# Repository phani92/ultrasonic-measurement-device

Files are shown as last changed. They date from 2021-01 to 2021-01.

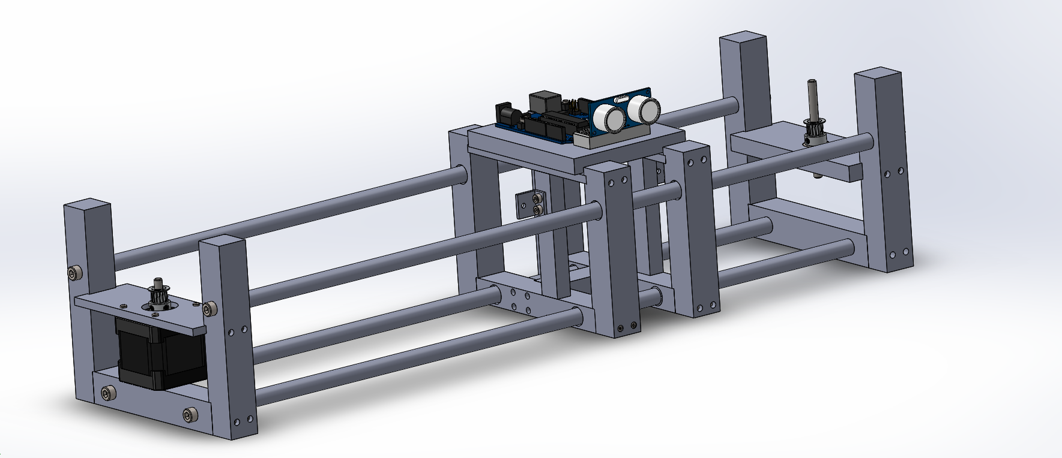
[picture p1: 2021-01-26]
cad files/assembly-bild.PNG

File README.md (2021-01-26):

# ultrasonic-measurement-device
A measurement setup using ultrasonic sensor and single axis linear system

Introduction:

Our aim for the scientific project was to develop a measurement setup that emits and receives ultrasound. The received data should be processed to a 1D ultrasound image. In addition, the influence of the control of the ultrasonic transmitter on the measured data is to be investigated.

Hence first we started with the basics of ultrasonic sensor its working principle and then we implemented the basic application of ultrasonic sensor for sensing distance with the help of Arduino and serial monitor. We displayed the distance real time in the serial monitor.

As per the problem statement, we need to now develop a measurement setup which can map sensor data. For this, we finalized on a linear guide system with Arduino as a slave and MATLAB as the main controller.

Ultrasonic Sensor:

Ultrasonic sensors emit short, high-frequency sound pulses at regular intervals. These propagate in the air at the velocity of sound. If they strike an object, then they are reflected as echo signals to the sensor, which itself computes the distance to the target based on the time- span between emitting the signal and receiving the echo.

As the distance to an object is determined by measuring the time of flight and not by the  intensity  of  the  sound,  ultrasonic  sensors  are  excellent  at  suppressing  background interference. Virtually all materials which reflect sound can be detected, regardless of their colour. Even transparent materials or thin foils represent no problem for an ultrasonic sensor. Ultrasonic sensors can see through dust-laden air and ink mists.

Even thin deposits on the sensor membrane do not impair its function. Sensors with a blind zone of only 20  mm and an extremely thin beam  spread are making entirely new applications possible today: Fill level measurement in wells of microtiter plates and test tubes, as well as the detection of small bottles in the packaging industry, can be implemented with ease. Even thin wires are reliably detected.



Mechanical Experimental Setup:

We selected a linear axis movement system so that the system can move automatically without any human errors or disturbance and the sensor can be studied more precisely and accurately. The idea of this system is to move it linearly in a single direction over a distance and to study the objects placed in its vicinity. The objects distance from this system and width of the object can be recorded with the help of ultrasonic sensor placed on the movable body.

Another advantage of this design is that we can study other sensors also by replacing the sensor and the respective program in Matlab. This design also gives a liberty to extend the observable area or study area by unbolting the ends and extending the linear guides.

In the initial phase of the project we have designed a single axis linear motion guide with the idea of using lead screw as shown below. The detachable holder with the ultrasonic sensor and Arduino setup can be placed over the moving unit in the above shown setup.



To have smooth movement such that the vibrations can be minimised and does not affect the study of sensor, the lead screw system was replaced with a pulley and belt system.

In the below figure, it can be noticed that the centre body is elevated to 5mm with respect to the corner holding stands. This is to allow the centre body to move freely. The idea of this setup is to pull the centre body from one end to another end with the help of a belt and a pulley system. Belt is hinged to the centre body.



The setup consists of three main mechanical parts.

1. Vertical Holding stands and linear guides

These stands are on both the corners of the setup and are heavy to give enough strength to the system such that the vibrations are absorbed, and the entire system stays stable on a surface. These stands are further drilled on 4 places so that the linear guides can be inserted into them and be bolted on the outer corners. There is also a flat plate on both the ends to mount the pulley and motor.

The pulley is mounted and free to rotate with the help of a ball bearing. The dimensions of these stands and bearings are provided in the design files that are attached in the appendix.



2. Centre Holding body

The centre body is to facilitate free movement for the sensor. This body lies on top of 4 linear guides. It has linear bearings to provide frictionless movement and is connected to the belt on both the ends which provide a pull force allowing for a movement in both the directions. The sensor along with Arduino and bread board for ultrasonic sensor are mounted on top of this setup. The entire metal frame holding the sensor and Arduino setup can be detached from the centre body by unbolting. It is feasible to use the sensor setup alone without the entire system. Just by unbolting two screws the sensor setup can be unmounted from the body.



3. Belt and pulley system

The belt is connected to both the ends of the centre of the body and the belt passes through the pulley and motor shaft thereby forming a closed-circuit system.  By pulling one of the ends of the body, it enables the body to travel in that direction. Nema 17 Stepper motor is used as it can provide a torque of 1.6 Kg / cm. The centre body weight around 700 grams and the torque provided by the motor is enough to move the body linearly.



The system was designed in SolidWorks and realised in workshop. All the files for individual tiles and the detail list of parts are shared in appendix. 

Solid Works Design:



Realised Setup:

Top View



Side View



Electronic Components:

We have used MATLAB platform to run our setup. Hence the Arduino Uno is used as a passive board. The electrical setup is as shown below.



The Electronic components used are: Ultrasonic sensor:

Here, we are using the HC-SR04 ultrasonic sensor. The big advantage of this sensor its available easily and very cheap compared to other ultrasonic sensors.



Specifications:

|Power Supply |+5V DC |
| - | - |
|Quiescent Current |<2mA |
|Working Current |15mA |
|Effectual Angle |<15 Degree |
|Ranging Distance |2-400 cm |
|Resolution |0.3 cm |
|Measuring Angle |30 Degree |
|Trigger Input Pulse width |10 s |
|Dimension |45mm x 20mm x 15mm |
|Weight approx |10 g |
Ultrasonic sensor has a transmitter and a receiver in one module. The transmitter has a piezo which vibrates at a frequency of 45 kHz. The working principle of this module is as shown in figure 1. The ultrasonic sensor is trigger by making Trigger pin high for 10us. Then 8 pulses of 40kHz is send and the echo is received by the receiver part of sensor. 



As discussed earlier, Ultrasonic sensor is used to detect the distance of an object. This is done by time of flight concept. Here we have a proportional relationship between time and distance.

Arduino Uno:

We established a communication between Arduino Uno and MATLAB. We first need to install Hardware support packages for Arduino Uno, HC-SR04 sensor. Once the Hardware packages are installed we can establish MATLAB and Arduino communication. Please see the appendix for the MATLAB code.

Arduino Uno is a microcontroller board based on the ATmega328P. It has 14 digital input/output pins (of which 6 can be used as PWM outputs), 6 analogue inputs, a 16 MHz quartz crystal, a USB connection, a power jack, an ICSP header and a reset button. It contains everything needed to support the microcontroller; simply connect it to a computer with a USB cable or power it with an AC-to-DC adapter or battery to get started.



Specifications:

|Microcontroller |ATmega328P |
| - | - |
|Operating voltage |5V |
|Number of Analog input pins |6 |
|Flash memory |32KB |
|Clock speed |16Mhz |
|DC current for 3.3v pin |50 mA |

Adafruit Motor shield v2.3:

The Motor shield is used as a driver for stepper motor. The stepper motor needs 0.33A of current to run at 12V DC. The Motor shield provides a 1.2A peak current per phase. We can connect 2 stepper motors with this shield at the same time. We have connected our Stepper motor at M1 and M2 as it’s a bipolar stepper motor.



Specifications :

- 2 connections for 5V 'hobby' servos connected to the Arduino's high-resolution dedicated timer - no jitter!
- 4 H-Bridges: TB6612 chipset provides 1.2A per bridge (3A for brief 20ms peaks) with thermal shutdown protection, internal kickback protection diodes. Can run motors on 4.5VDC to 13.5VDC.
- Up to 4 bi-directional DC motors with individual 8-bit speed selection (so, about 0.5% resolution)
- Up to 2 stepper motors (unipolar or bipolar) with single coil, double coil, interleaved or micro-stepping.
- Motors automatically disabled on power-up
- Big terminal block connectors to easily hook up wires (18-26AWG) and power
- Arduino reset button brought up top
- Polarity protected 2-pin terminal block and jumper to connect external power, for separate logic/motor supplies
- Tested compatible with Arduino UNO, Leonardo, ADK/Mega R3, Diecimila & Duemilanove. Works with Due with 3.3v logic jumper. Works with Mega/ADK R2 and earlier with 2 wire jumpers.
- 5v or 3.3v compatible logic levels - jumper configurable.

Stepper motor:

We have used a NEMA 17 stepper motor with 1.8-degree angle per step. The electrical specification of stepper motor is as follows:

|Step angle |1.8 degree |
| - | - |
|Phases |2 |
|Insulation Resistance |100Mohms (500V DC) |
|Class of Insulation |B |
|Weight |0.20 Kg |
|Voltage |12V |
|Current |0.33A |
|Holding torque |0.23 Nm |
The stepper motor has 2 coils and it’s a 4-wire motor. It is wired to Motor shield as shown below.



Power Supply:

We need power to run the entire setup. 5v DC power to run the Arduino and 12V to power the shield which provides the required voltage and current for the motors.

The Arduino is powered with the help of a USB cable and as we track live data, it can be controlled with Matlab. The Arduino acts as a slave to Matlab. The Shield is provided with external power source with the help of an adapter. These both power sources are enough to run the entire setup and collect data from the sensor.

Calculations:

Before executing the program to run the motor, we need to do following calculations.

- Steps Per mm:

This will help us estimate how many steps our motor must travel to achieve 1mm practically.

For Belt and Pulley Setup:

Steps / mm  =  ( ) ∗( )

( − ℎ) ∗( ℎ)

We are using GT2 belt with a pulley having 20 teeth. Motor Steps per rev = 200

Driver micro stepping = 1

Belt pitch = 2mm

Pulley Teeth = 20

Steps / mm = 200 ∗1 = 5

(2) ∗(20)

For loops in Matlab = (Steps/mm) \* (distance) = 5 \* 450 = 2250

- Maximum speed of motor:

Max Speed = ( ∗ 60)/( ∗ 2 ∗ ∗ )

- 12 \* 60 / (1.2 \* 2 \* 0.33 \* 200)
- 4.5 mm / s

Note: In Matlab code, number of loops is 450 and the linear displacement given is 5 which results in 2250 as per our calculation above.

Range of sensor:



Measurements:

1. Experiment with a metal stand (30 cm distance):



Result:



The above plot was mapped in Matlab and it can be seen the distance to be approximately 30 cm.

2. Experiment with a wooden stand (70 cm distance):



Results:



It can be seen in the above figure that wood is placed exactly at 70 cm and the output graph is also nearby to 70 cm.

Observations:

- The ultrasonic sensor detects all the objects in this range at a beam angle of 15 degrees. Hence the object width calculation is a tricky job with this ultrasonic sensor.
- As per the time of flight concept the measured distance is directly proportional to the time. Time is inversely proportional to frequency. Hence by varying the frequency of the piezo crystal the range of ultrasonic sensor will be varied.
- Ultrasonic sensor can give false echoes of object places at different distance. This can be solved by using the ultrasonic sensor with low frequency by which the false echoes will diminished before reaching the receiver.
- Objects which are place at an angle will cause the deflection of echoes. Hence the objects should always be present perpendicular.
- There is also an effect of temperature. As temperature increases the detecting range decreases. Hence in some of the commercial products they have temperature compensation circuit available.

Future scope:

- The communication can be made wireless.
- With the existing setup we can plug other sensor for distance measurement and mapping environment. Sensors with high accuracy and less beam angle.

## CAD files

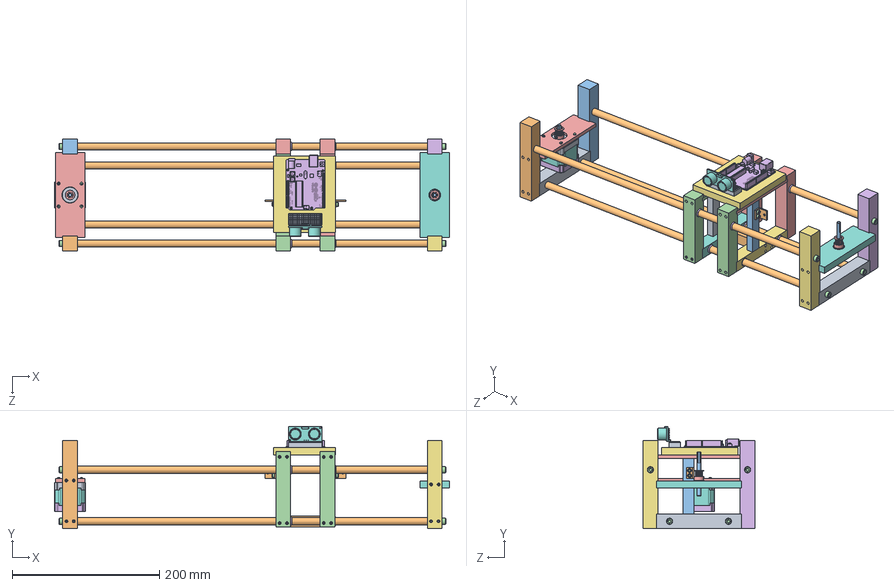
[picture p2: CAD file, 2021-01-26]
cad files/Assembly/Ultrasonic-assembly.SLDASM
536.8 x 139.0 x 152.0 mm
vertical stand bottom piece x 2
vertical stand holder left
vertical stand holder right
socket head cap screw_am x 73
motor holding plate
nema17_bottom_40mm
radial ball bearing_68_din x 2
nema17_middle_40mm
nema17_top_40mm
countersunk flat head cross recess screw_din x 4
nema17_shaft_40mm x 2
pan cross head_am x 4
GT2_16T_13x14 x 2
vertical stand holder left pulley
vertical stand holder right pulley
pulley holding plate
instrument ball bearing_68_am
centre holding horizontal plate
vertical stand holder centre left x 2
vertical stand holder right centre block x 2
linear bearing cheap x 8
vertical centre stand bottom left piece
vertical centre stand bottom piece
belt holder 2
Belt mounting x 2
belt holder 1
centre tower holding plate
centre tower holding plate right
Arduino UNO
equipment holder
hc sr04 ultrasonic sensor
MiniBreadboard
bottom centre support
pan slot head_am x 4

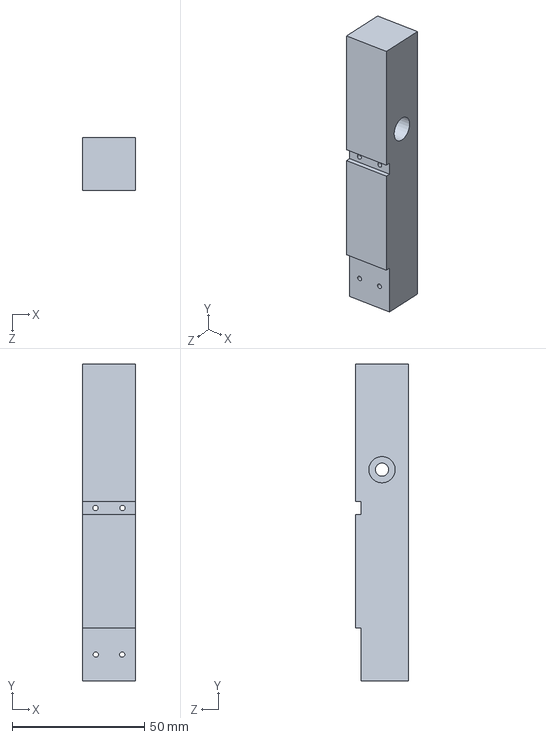
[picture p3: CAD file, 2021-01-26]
cad files/Teil-1/1.vertical stand holder right.SLDPRT
20.0 x 120.0 x 20.0 mm

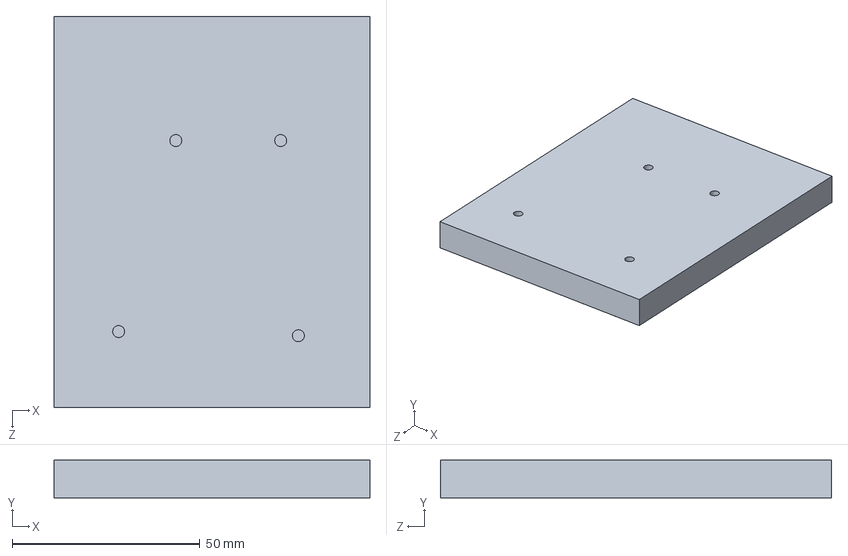
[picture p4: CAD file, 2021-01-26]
cad files/Teil-10/10.equipment holder.SLDPRT
84.0 x 10.0 x 104.0 mm

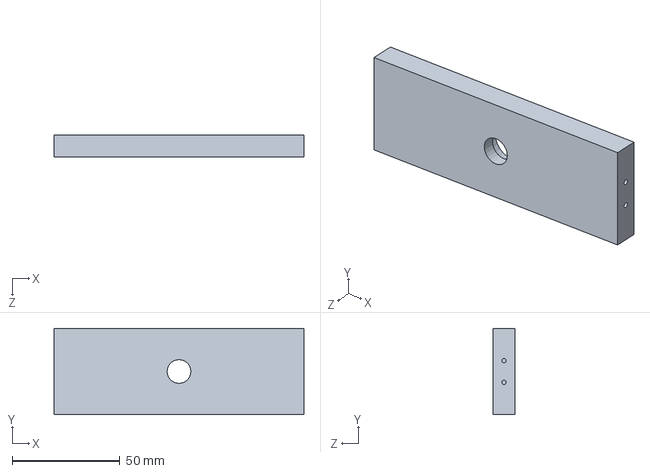
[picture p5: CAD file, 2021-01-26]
cad files/Teil-11/11.pulley holding plate.SLDPRT
116.0 x 40.0 x 10.0 mm

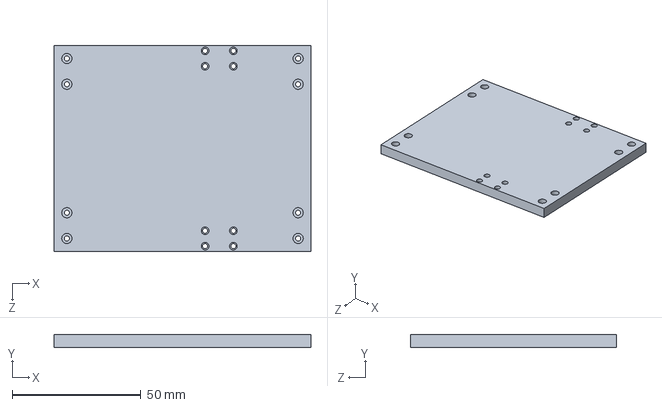
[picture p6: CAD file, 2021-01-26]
cad files/Teil-12/12.centre holding horizontal plate.SLDPRT
100.0 x 5.00 x 80.0 mm

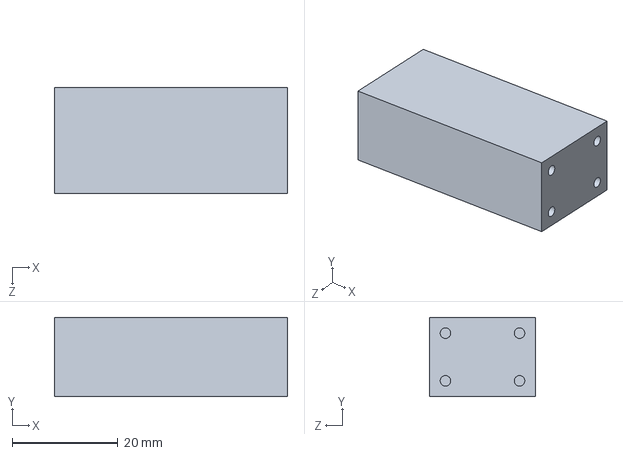
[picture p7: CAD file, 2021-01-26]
cad files/Teil-13/13.bottom centre support.SLDPRT
44.0 x 15.0 x 20.0 mm

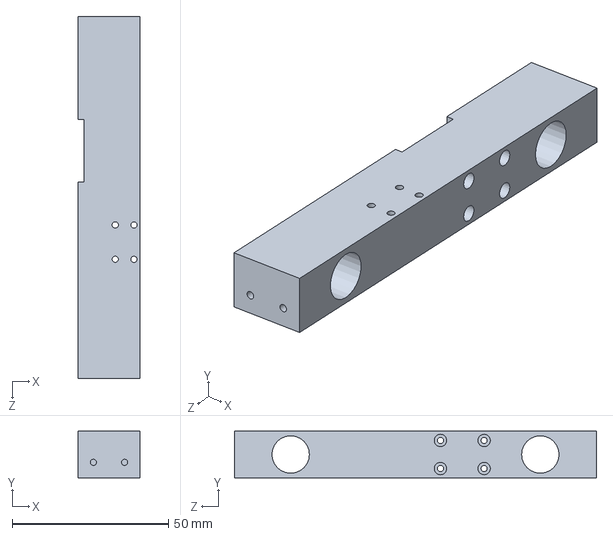
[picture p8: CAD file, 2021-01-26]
cad files/Teil-14/14.vertical centre stand bottom left piece.SLDPRT
20.0 x 15.0 x 116.0 mm

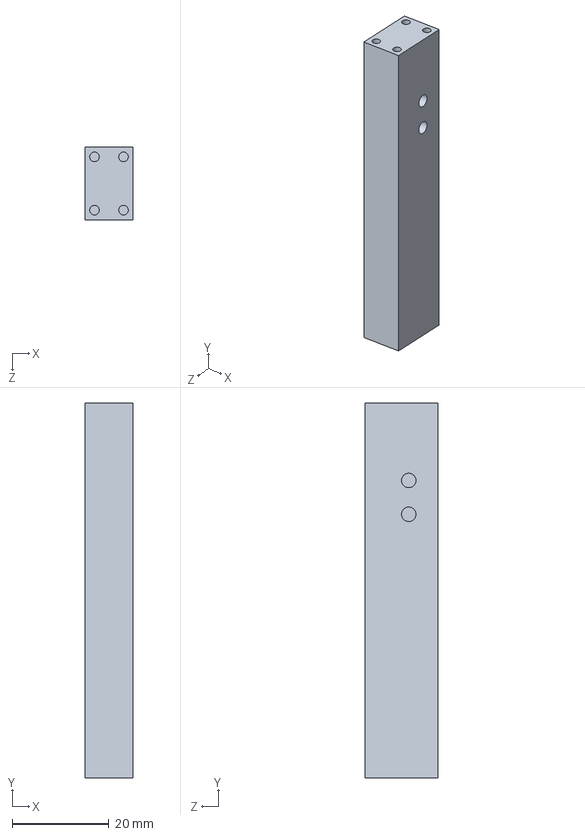
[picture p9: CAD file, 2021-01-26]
cad files/Teil-15/15.belt holder 1.SLDPRT
10.0 x 77.5 x 15.0 mm

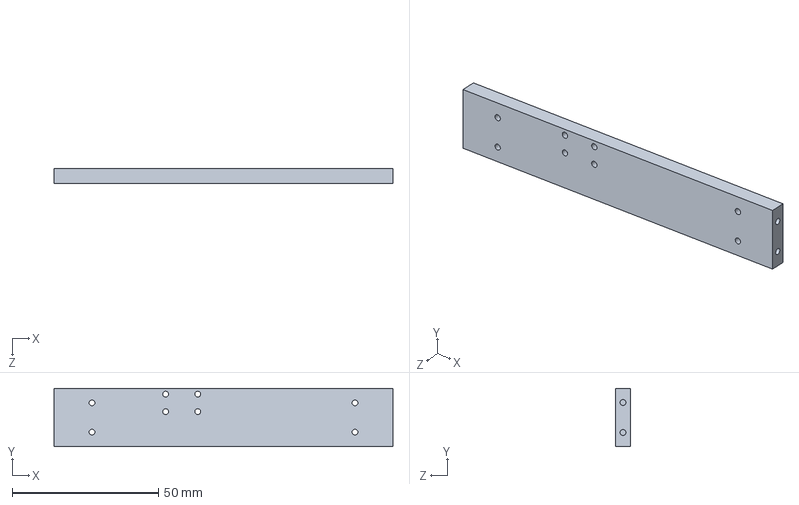
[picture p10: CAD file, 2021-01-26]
cad files/Teil-16/16.centre tower holding plate right.SLDPRT
116.0 x 20.0 x 5.00 mm

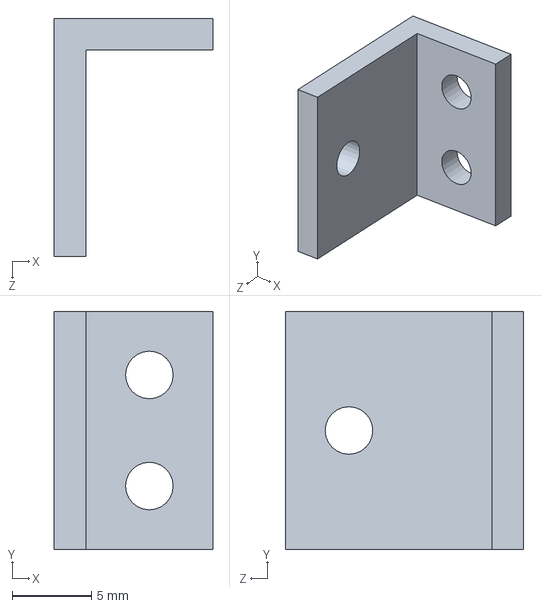
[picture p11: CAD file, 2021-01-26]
cad files/Teil-17/17.Belt mounting.SLDPRT
10.0 x 15.0 x 15.0 mm

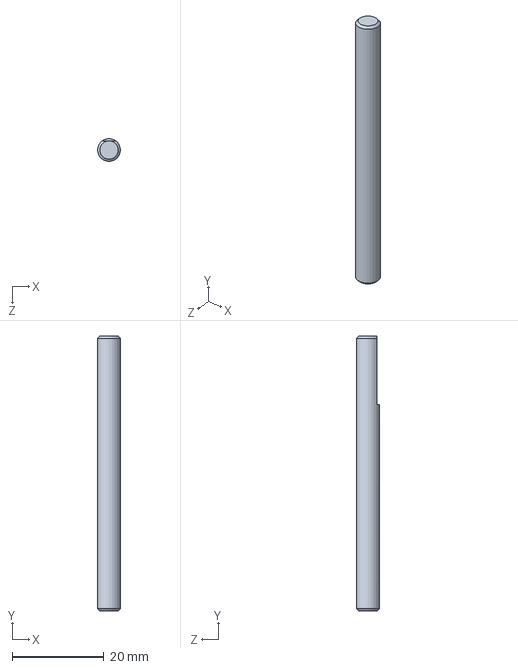
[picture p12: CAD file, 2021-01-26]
cad files/Teil-20/20.nema17_shaft_40mm.SLDPRT
5.00 x 60.0 x 5.00 mm

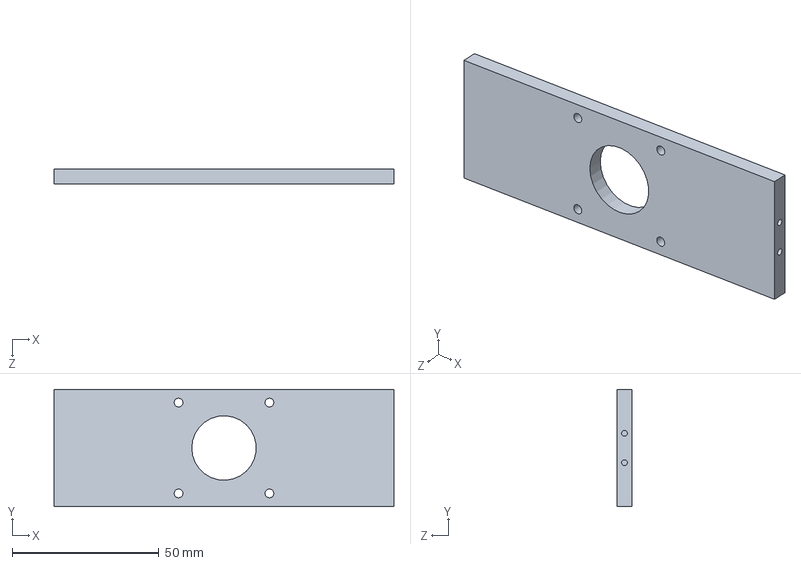
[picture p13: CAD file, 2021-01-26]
cad files/Teil-4/4.motor holding plate.SLDPRT
116.0 x 40.0 x 5.00 mm

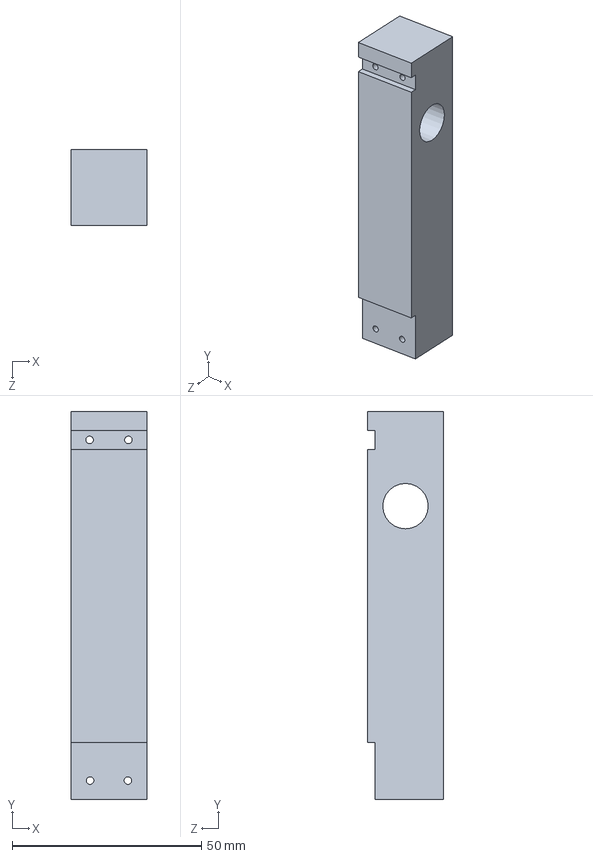
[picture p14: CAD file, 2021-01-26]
cad files/Teil-5/5.vertical stand holder right centre block.SLDPRT
20.0 x 102.5 x 20.0 mm

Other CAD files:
cad files/Teil-18/18.vertical stand holder left pulley.SLDPRT
cad files/Teil-19/19.vertical stand holder right pulley.SLDPRT
cad files/Teil-2/2.vertical stand holder left.SLDPRT
cad files/Teil-3/3.vertical stand bottom piece.SLDPRT
cad files/Teil-6/6.vertical stand holder centre left.SLDPRT
cad files/Assembly/Ultrasonic assembly.SLDDRW
cad files/Teil-1/1.vertical stand holder right.SLDDRW
cad files/Teil-10/10.equipment holder.SLDDRW
cad files/Teil-11/11.pulley holding plate.SLDDRW
cad files/Teil-12/12.centre holding horizontal plate.SLDDRW
cad files/Teil-13/13.bottom centre support.SLDDRW
cad files/Teil-14/14.vertical centre stand bottom left piece.SLDDRW
cad files/Teil-15/15.belt holder 1.SLDDRW
cad files/Teil-16/16.centre tower holding plate right.SLDDRW
cad files/Teil-17/17.Belt mounting.SLDDRW
cad files/Teil-18/18.vertical stand holder left pulley.SLDDRW
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

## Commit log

2021-01-26 removes the md file for ultrasonic sensor as the data was moved to readme. #1
2021-01-26 Adds cad files. #1
    [1.vertical stand holder right.SLDDRW, 1.vertical stand holder right.SLDPRT, 10.equipment holder.SLDDRW, 10.equipment holder.SLDPRT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]
